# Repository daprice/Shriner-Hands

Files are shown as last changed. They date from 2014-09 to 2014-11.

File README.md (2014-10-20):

#Low Profile Thumb Prosthesis

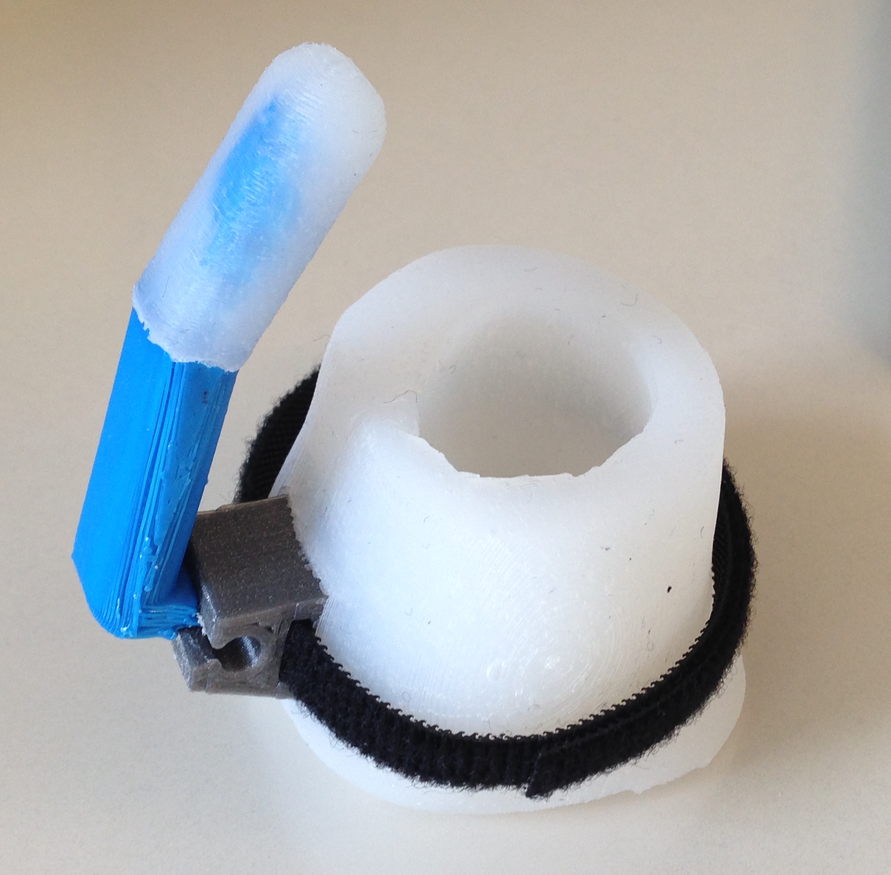
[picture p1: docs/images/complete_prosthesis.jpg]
Photo of assembled prosthesis


This prosthesis is designed to provide a static thumb post for patients who have one or more fingers with a good range of motion, but no thumb to oppose against. The prosthesis consists of a silicone sleeve that goes around the patient's palm, tightened by a velcro strap. A mounting point for a static thumb post (optionally with a grippy silicone cover) is molded into the sleeve.

See the [assembly documentation](http://daprice.github.io/Shriner-Hands/docs/documentation.html) for more information and instructions for configuring and assembling one.

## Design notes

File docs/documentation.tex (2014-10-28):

\documentclass[11pt]{article}
\usepackage[latin2]{inputenc}
\usepackage{a4wide}
\usepackage{graphicx}
\usepackage{hyperref}
\hypersetup{colorlinks=true,linkcolor=blue}
\title{Low Profile Thumb Prosthesis Documentation}
\author{ThingDoc}

\begin{document}

\maketitle
\begin{center}
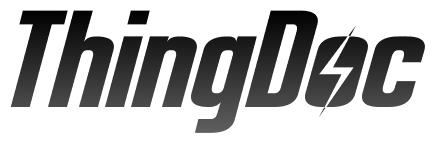
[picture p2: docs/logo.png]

\end{center}
This prosthesis is designed to provide a static thumb post for patients who have one or more fingers with a good range of motion, but no thumb to oppose against. The prosthesis consists of a silicone sleeve that goes around the patient's palm, tightened by a velcro strap. A mounting point for a static thumb post (optionally with a grippy silicone cover) is molded into the sleeve.

\newpage

\tableofcontents

\newpage

\section{Bill of Materials}
List of things you need to build the machine divided by categories.

\subsection{Prerequisites!}
\begin{itemize}
\item 1x \hyperlink{thing_hand\_scan}{3D scan of patient's hand}
\end{itemize}

\subsection{Materials}
\begin{itemize}
\item 100x \hyperlink{thing_g\_dragon\_skin\_30}{grams of Dragon Skin 30 liquid silicone}
\item 10x \hyperlink{thing_g\_dragon\_skin\_10}{grams of Dragon Skin 10 liquid silicone}
\end{itemize}

\subsection{Fasteners}
\begin{itemize}
\item 4x M4 Hex Nut
\item 1x \hyperlink{thing_velcro\_strap}{Velcro Strap}
\item 6x Piece of Tape
\item 4x M4x15 Bolt
\end{itemize}

\subsection{Printed}
\begin{itemize}
\item 2x \hyperlink{thing_rigid\_base}{Rigid base with thumb}
\item 1x \hyperlink{thing_mold\_left\_half}{Mold - left half}
\item 1x \hyperlink{thing_truncated\_hand}{Truncated Print of Patient's Hand}
\item 1x \hyperlink{thing_thumb\_mold}{Thumb Mold}
\item 1x \hyperlink{thing_mold\_right\_half}{Mold - right half}
\end{itemize}

\newpage

\section{Things Overview}
List of things and their descriptions.

\hypertarget{thing_config\_file}{\subsection{Configuration and Rendering of 3D models}}
Configuration settings for the Shriners Hand, required to generate correct STLs of the printed parts. See the Configuration File Assembly instructions to set this up.

\hypertarget{thing_rigid\_base}{\subsection{Rigid base with thumb}}
3D printed rigid base and static thumb post - rendered from src/scad/rigid_base.scad


\hypertarget{thing_silicone\_sleeve}{\subsection{Silicone sleeve}}
Silicone sleeve that goes over the patient's palm

\hypertarget{thing_molded\_thumb}{\subsection{Thumb with Molded Grip}}
Molded silicone thumb pad can improve grip and provide some tactile feedback to the wearer

\hypertarget{thing_truncated\_hand}{\subsection{Truncated Print of Patient's Hand}}
Shortened and resized portion of the patient's palm to be the center of the mold during silicone casting - rendered from src/scad/truncated_hand.scad (example shown)


\hypertarget{thing_thumb\_mold}{\subsection{Thumb Mold}}
Mold for casting the silicone finger tip grip - rendered from src/inventor/thumb_mold.ipt


\hypertarget{thing_g\_dragon\_skin\_10}{\subsection{grams of Dragon Skin 10 liquid silicone}}
Dragon Skin 10 silicone resin kit, available from Smooth-On. Shore A durometer (hardness) 10.
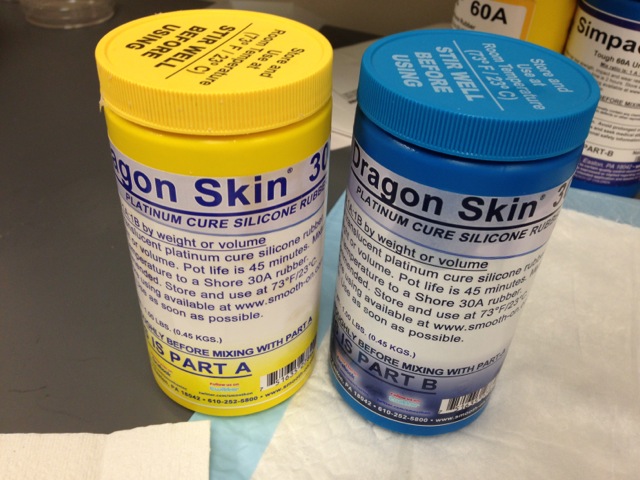
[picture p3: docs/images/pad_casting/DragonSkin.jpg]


\hypertarget{thing_mold\_right\_half}{\subsection{Mold - right half}}
Right half of 3D printed mold for casting the silicone sleeve - rendered from src/scad/mold_right.scad


\hypertarget{thing_mold\_left\_half}{\subsection{Mold - left half}}
Left half of 3D printed mold for casting the silicone sleeve - rendered from src/scad/mold_left_half.scad


\hypertarget{thing_g\_dragon\_skin\_30}{\subsection{grams of Dragon Skin 30 liquid silicone}}
Dragon Skin 30 silicone resin kit, available from Smooth-On. Shore A durometer (hardness) 30.


\hypertarget{thing_velcro\_strap}{\subsection{Velcro Strap}}
9mm wide velcro strap of adequate length to wrap around the patient's palm with at least 30% extra.

\hypertarget{thing_hand\_scan}{\subsection{3D scan of patient's hand}}
3D scan of the patient's hand with wrist and finger(s) held straight. Must be a manifold mesh (STL file); may be simplified for faster processing. Place in userScans directory before configuring and rendering OpenSCAD models.

\hypertarget{thing_mold\_assembly}{\subsection{Palm Sleeve Mold Assembly}}
Assembled mold for casting the silicone sleeve

\newpage

\section{Assembly Instructions}

\subsection{Assemble Configuration and Rendering of 3D models}
Things needed:
\begin{itemize}
\item 1x \hyperlink{thing_hand\_scan}{3D scan of patient's hand}
\end{itemize}
Steps:
\begin{enumerate}
\item Place a manifold, cleaned-up version of the patient's hand scan (if necessary, the model can be repaired using Netfabb) in the userScans folder.
\item Open src/scad/configuration.scad in your favorite text editor.
\item Type the filename of the patient's hand scan in place of "JudahLeftHandShortened.stl" in the configuration file.
\item Open src/scad/alignment.scad using OpenSCAD so you can see the placement of the 3D model while you edit the configuration file. (you may have to manually press the Reload and Preview button every time you make a change to the configuration file)
\item In configuration.scad, change the hand\_d parameter to the diameter of the thickest part of the patient's hand in mm.
\item Adjust the hand\_pos (position of the hand in 3D space) and hand\_rot (rotation of hand around each axis) parameters so that the 3D scan of the hand is aligned with the arrows as described in the following 2 steps.
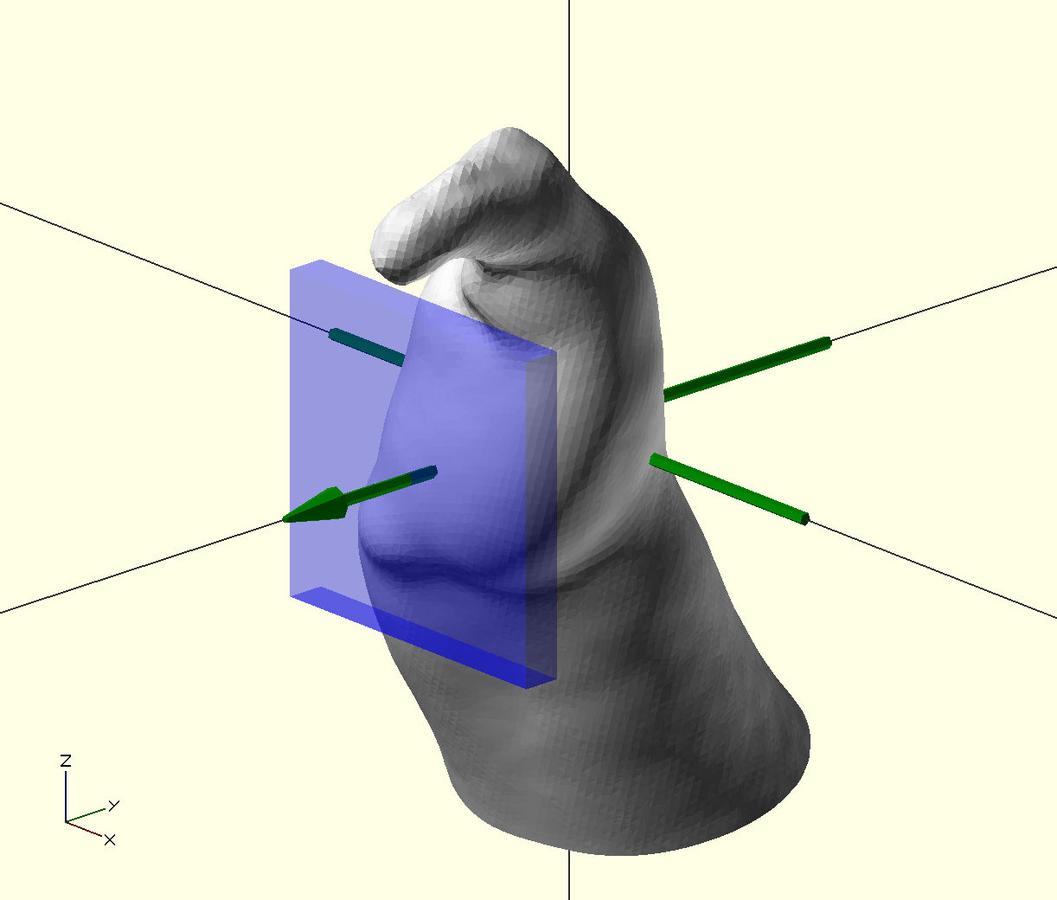
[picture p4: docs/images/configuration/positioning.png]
\item The palm of the hand should be roughly vertical, centered on the green crosshair as much as possible, and the hand should be oriented so that the patient's finger(s) flex toward the green arrow.\\ 
\item The palmar surface should be just within the blue area when viewed from the side.\\ 
\item (Optional) Adjust the other parameters in the configuration file to control the dimensions of various parts of the prosthesis. The default values should work most of the time.
\item After you have aligned the hand, open src/scad/preview.scad in OpenSCAD to ensure that all parts of the prosthesis look correct.\\ 
\item Open each part to be printed (from the src/scad folder) in OpenSCAD, render each one (F6) and export as STL, then print using the STL files. Recommended print settings are 0.2mm or smaller layer height, three perimeters, three top and bottom solid layers, 40\% rectilinear or hexagonal infill, and support material enabled.
\end{enumerate}

\subsection{Assemble Palm Sleeve Mold Assembly}
Things needed:
\begin{itemize}
\item 1x \hyperlink{thing_config\_file}{Configuration and Rendering of 3D models}
\item 4x M4 Hex Nut
\item 1x \hyperlink{thing_mold\_left\_half}{Mold - left half}
\item 1x \hyperlink{thing_rigid\_base}{Rigid base with thumb}
\item 4x Piece of Tape
\item 1x \hyperlink{thing_mold\_right\_half}{Mold - right half}
\item 4x M4x15 Bolt
\end{itemize}
Steps:
\begin{enumerate}
\item Set one half of the mold on a flat surface with the flat side down.
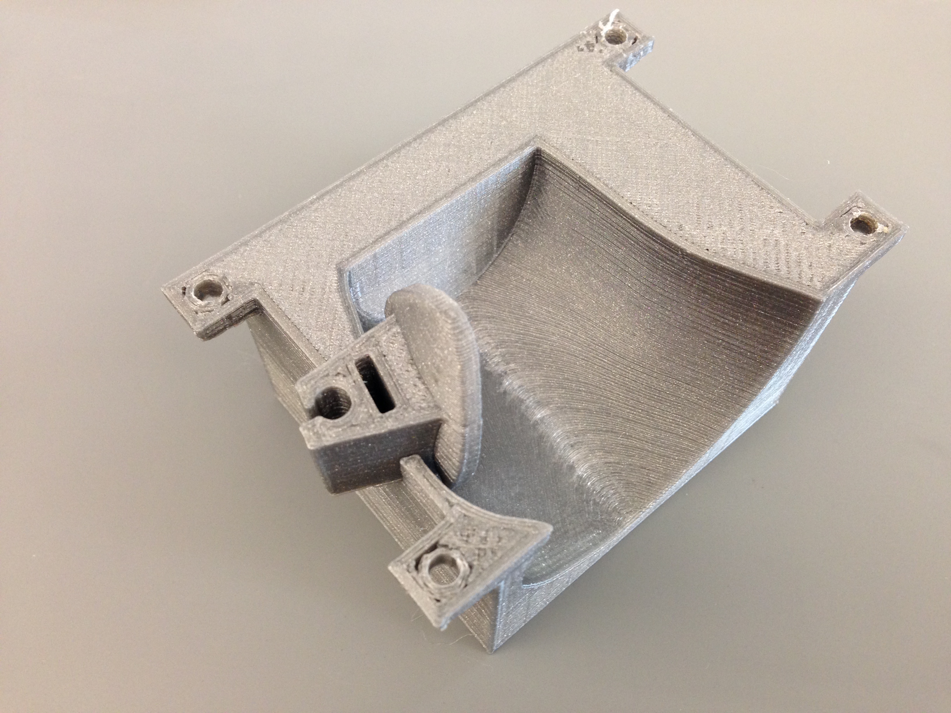
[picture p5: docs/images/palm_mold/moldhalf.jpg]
\item Insert the rigid thumb base into the slot in the side of the mold, with the round part toward the inside and the shorter prong toward the closed end of the mold.\\ 
\item Set the other half of the mold with the flat side up so the two halves align.
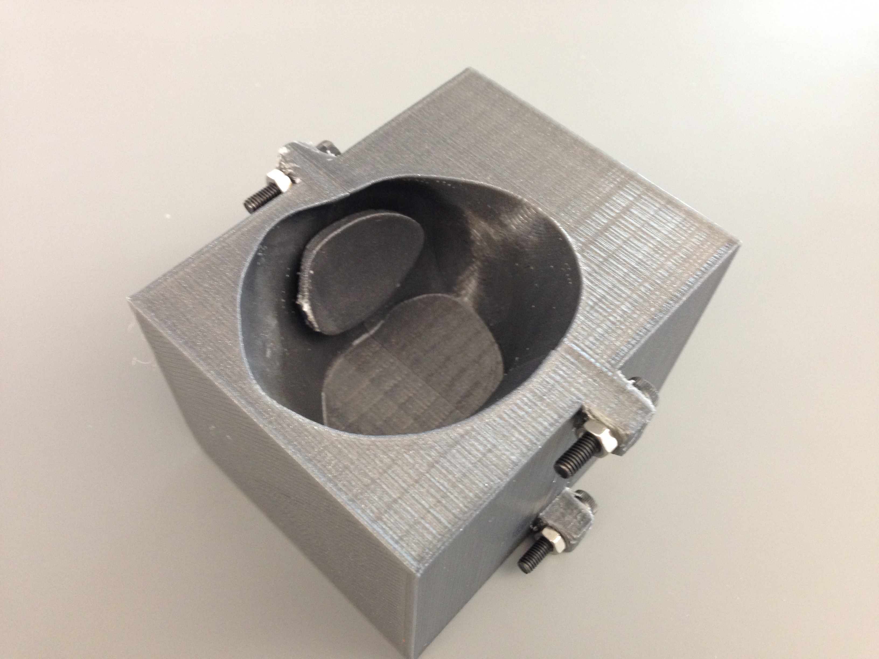
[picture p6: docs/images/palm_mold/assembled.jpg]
\item Fasten the two halves together using the nuts and bolts in the holes at each corner.\\ 
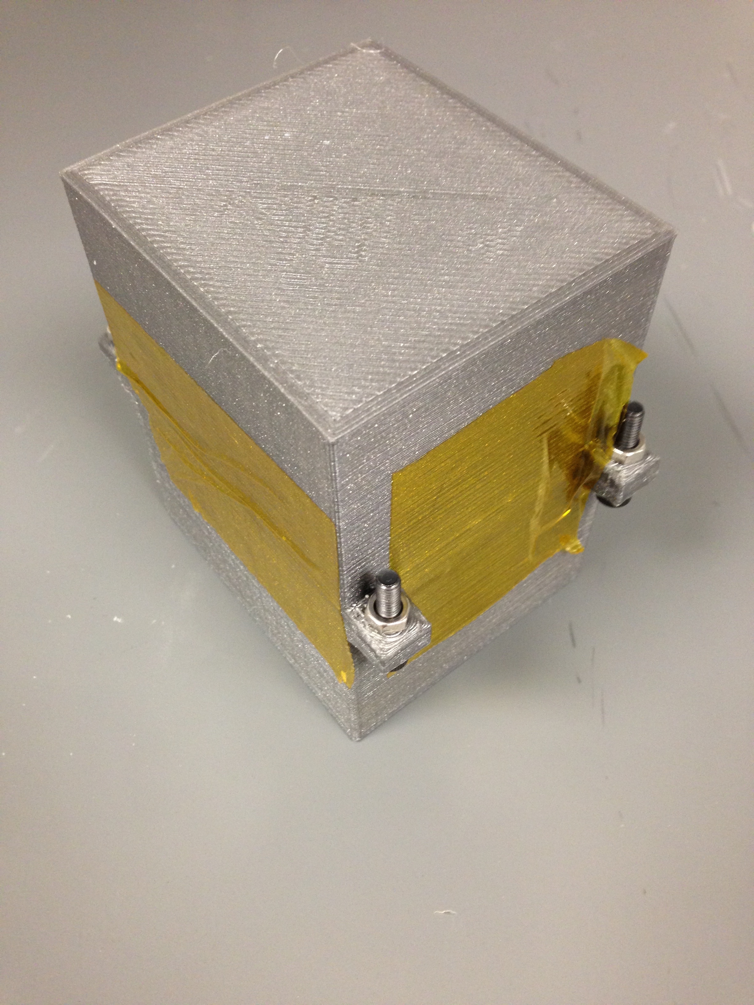
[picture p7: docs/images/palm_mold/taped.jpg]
\item (Optional) use tape to seal the seams on the outside of the mold to prevent leakage.\\ 
\end{enumerate}

\subsection{Assemble Silicone sleeve}
Things needed:
\begin{itemize}
\item 100x \hyperlink{thing_g\_dragon\_skin\_30}{grams of Dragon Skin 30 liquid silicone}
\item 1x \hyperlink{thing_mold\_assembly}{Palm Sleeve Mold Assembly}
\item 1x \hyperlink{thing_truncated\_hand}{Truncated Print of Patient's Hand}
\item 2x Piece of Tape
\end{itemize}
Steps:
\begin{enumerate}
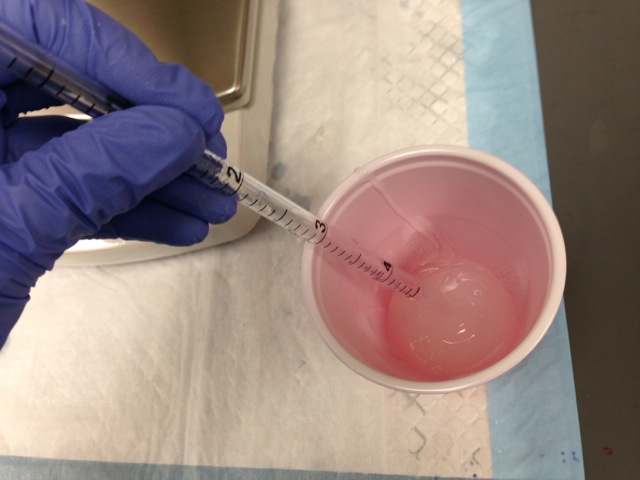
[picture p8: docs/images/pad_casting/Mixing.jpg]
\item Mix silicone according to the instructions from the supplier. Wear gloves and follow the supplier's safety guidelines while working with liquid silicone.\\ 
\item Insert the truncated hand (automatically sized by truncated\_hand.scad) in the opening of the mold, narrow side down, so that it sits in the center of the mold and lines up with the overall shape of the mold. Make sure there is a small gap between the truncated hand and the thumb base piece.\\ 
\item Tape the truncated hand in place to prevent it from moving or floating when the silicone is poured. Leave some space around it open to pour the silicone and for air to escape.\\ 
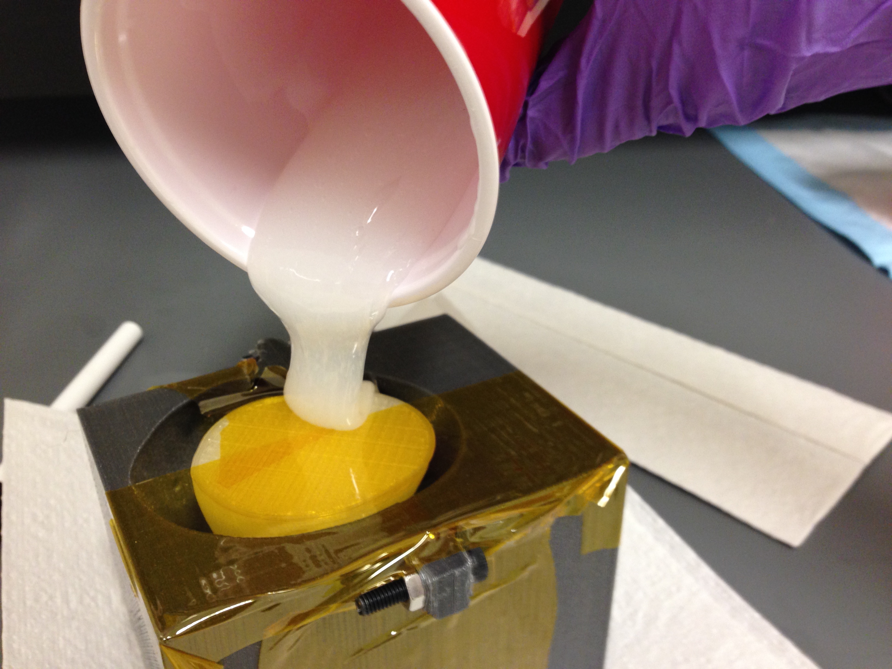
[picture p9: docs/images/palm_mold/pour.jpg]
\item Pour the liquid silicone to fill the mold. Make sure it settles to the bottom and completely surrounds the printed hand.\\ 
\item After the silicone cures (16 hours if using Dragon Skin 30), unscrew and separate the two halves of the mold, and pull out the truncated hand.
\item If necessary, use a knife to cut off any excess silicone and/or cut the sleeve to better fit the patient's hand.
\end{enumerate}

\subsection{Assemble Thumb with Molded Grip}
Things needed:
\begin{itemize}
\item 1x \hyperlink{thing_rigid\_base}{Rigid base with thumb}
\item 10x \hyperlink{thing_g\_dragon\_skin\_10}{grams of Dragon Skin 10 liquid silicone}
\item 1x \hyperlink{thing_thumb\_mold}{Thumb Mold}
\end{itemize}
Steps:
\begin{enumerate}
\item Print the skeletal thumb and mold.
\item Mix silicone according to the instructions from the supplier. Wear gloves and follow the supplier's safety guidelines while working with liquid silicone.\\ 
\item Pour the liquid silicone to mostly fill the thumb mold.
\item Insert the printed skeletal thumb into the filled mold as far as it will go.
\item Remove most of the excess silicone. Small amounts of excess can be removed afer molding.
\item After the silicone has cured (up to 7 hours if using Dragon Skin 10 Slow), carefully pull the thumb to remove it from the mold.
\item If necessary, use a knife to trim off excess silicone so that the edges of the silicone part are flush with those of the hard printed part.
\end{enumerate}

\subsection{Assemble Low Profile Thumb Prosthesis}
Things needed:
\begin{itemize}
\item 1x \hyperlink{thing_silicone\_sleeve}{Silicone sleeve}
\item 1x \hyperlink{thing_molded\_thumb}{Thumb with Molded Grip}
\item 1x \hyperlink{thing_velcro\_strap}{Velcro Strap}
\end{itemize}
Steps:
\begin{enumerate}
\item Insert the thumb into the slot on the base.
\item Insert the velcro strap through the slot on the base.
\item (Optional) If the velcro strap does not fit well around the silicone sleeve, use a knife to cut slits into the sides of the sleeve, then route the velcro sleeve through the slits.
\item Insert patient's hand into the sleeve.
\item Fasten the velcro strap and tighten as needed to hold the prosthesis in place during use.
\end{enumerate}

\newpage

\end{document}

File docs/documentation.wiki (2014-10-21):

== Bill of Materials ==

=== Prerequisites! ===
{| class="wikitable sortable" border="1"
|-
! scope="col" | Quantity
! scope="col" | Description
! scope="col" | Type
! scope="col" class="unsortable" | Comments
! scope="col" class="unsortable" | Diagram
|-
| 1 || 3D scan of patient's hand ||  ||  ||
|}

=== Materials ===
{| class="wikitable sortable" border="1"
|-
! scope="col" | Quantity
! scope="col" | Description
! scope="col" | Type
! scope="col" class="unsortable" | Comments
! scope="col" class="unsortable" | Diagram
|-
| 100 || grams of Dragon Skin 30 liquid silicone ||  ||  || 50px
|-
| 10 || grams of Dragon Skin 10 liquid silicone ||  ||  || 50px
|}

=== Fasteners ===
{| class="wikitable sortable" border="1"
|-
! scope="col" | Quantity
! scope="col" | Description
! scope="col" | Type
! scope="col" class="unsortable" | Comments
! scope="col" class="unsortable" | Diagram
|-
| 4 || M4 Hex Nut ||  ||  ||
|-
| 1 || Velcro Strap ||  ||  ||
|-
| 6 || Piece of Tape ||  ||  ||
|-
| 4 || M4x15 Bolt ||  ||  ||
|}

=== Printed ===
{| class="wikitable sortable" border="1"
|-
! scope="col" | Quantity
! scope="col" | Description
! scope="col" | Type
! scope="col" class="unsortable" | Comments
! scope="col" class="unsortable" | Diagram
|-
| 2 || Rigid base with thumb ||  ||  || 50px
|-
| 1 || Mold - left half ||  ||  || 50px
|-
| 1 || Truncated Print of Patient's Hand ||  ||  || 50px
|-
| 1 || Thumb Mold ||  ||  || 50px
|-
| 1 || Mold - right half ||  ||  || 50px
|}

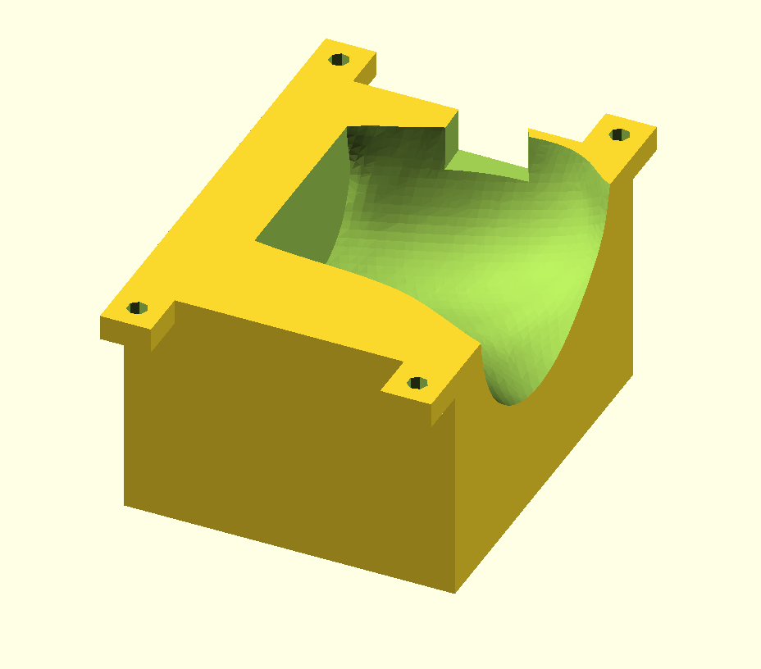
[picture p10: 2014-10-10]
docs/images/mold_right_half.png

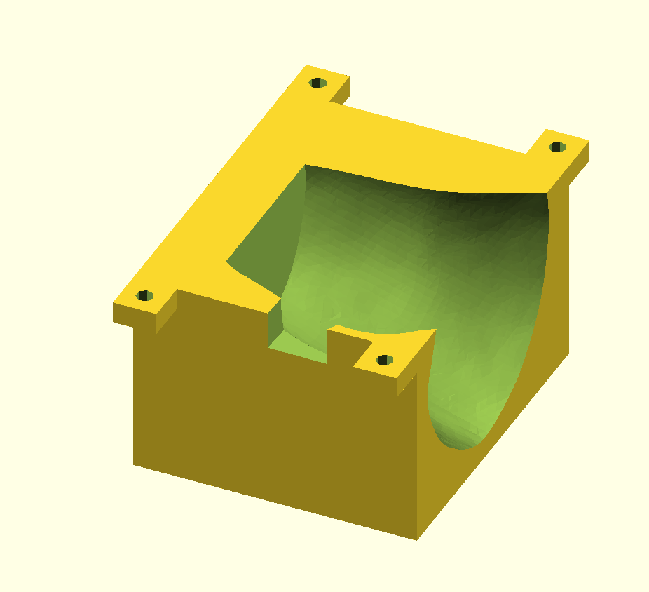
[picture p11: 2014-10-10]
docs/images/mold_left_half.png

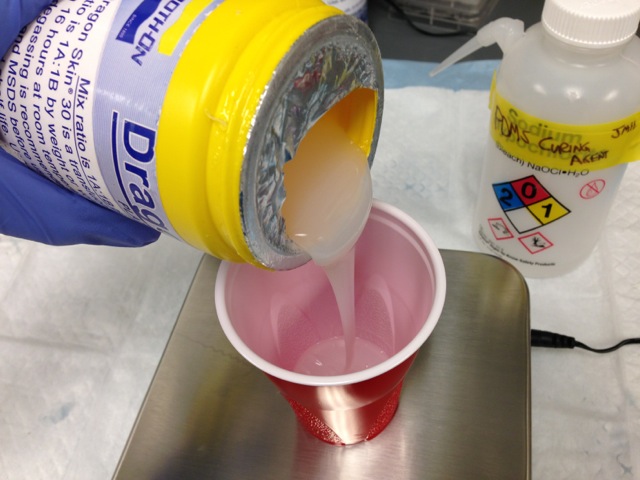
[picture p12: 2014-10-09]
docs/images/pad_casting/Pouring part A.jpg

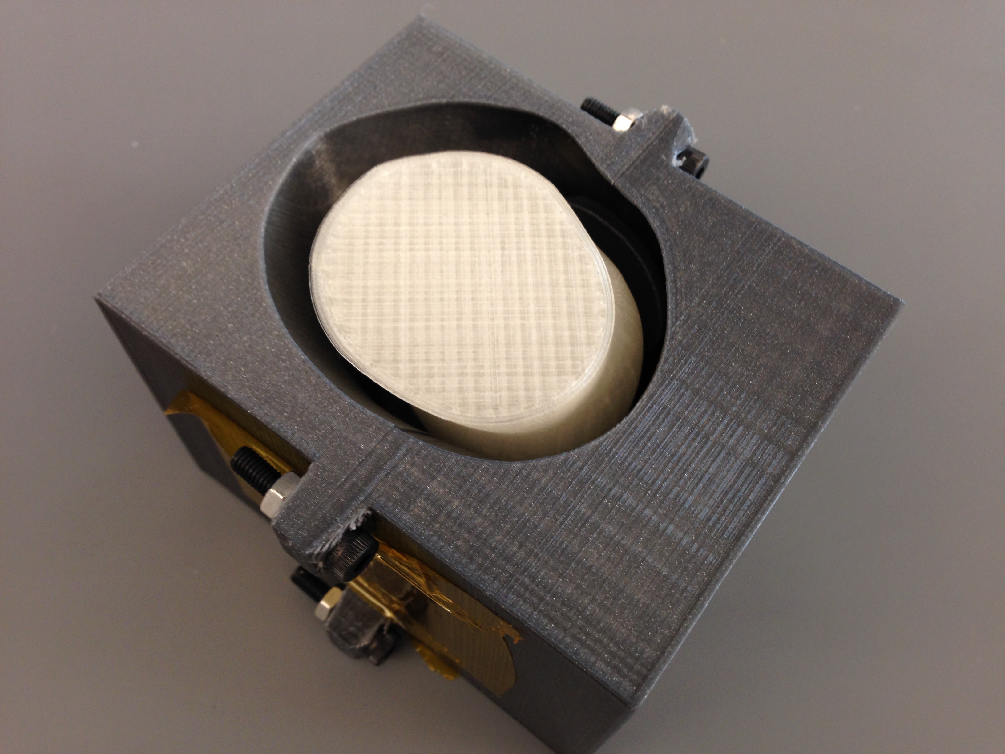
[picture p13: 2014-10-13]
docs/images/palm_mold/hand_in_mold.jpg

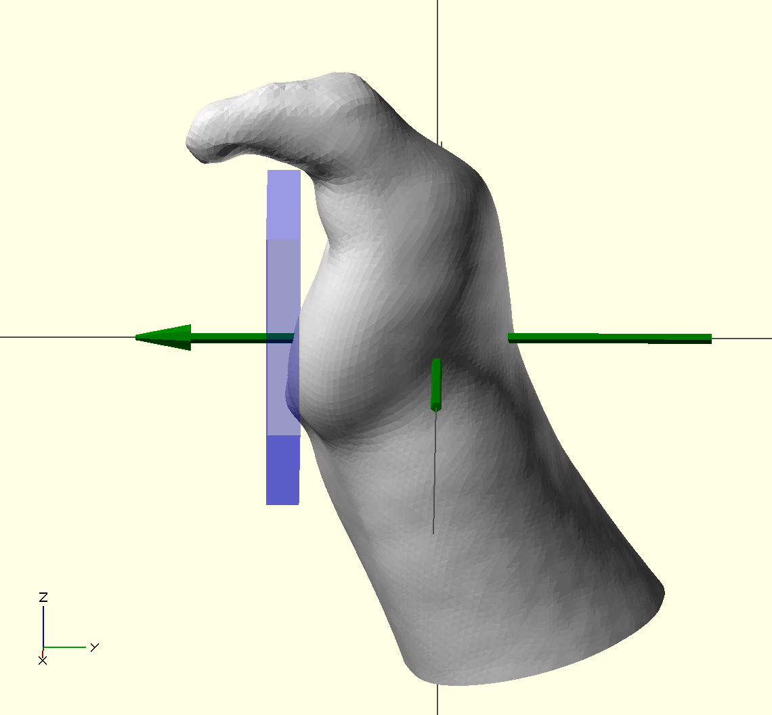
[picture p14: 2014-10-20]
docs/images/configuration/forward_alignment.png

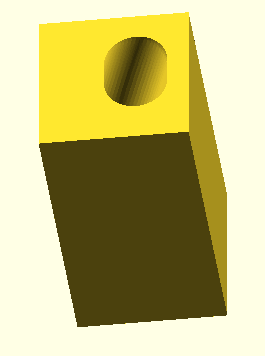
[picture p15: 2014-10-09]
docs/images/thumb_mold.png

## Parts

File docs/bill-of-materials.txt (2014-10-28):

Bill of Materials: Low Profile Thumb Prosthesis
+++++++++++++++++++++++++++++++++++++++++++++++

Prerequisites!
==============
- 1x 3D scan of patient's hand

Materials
=========
- 100x grams of Dragon Skin 30 liquid silicone
- 10x grams of Dragon Skin 10 liquid silicone

Fasteners
=========
- 4x M4 Hex Nut
- 1x Velcro Strap
- 6x Piece of Tape
- 4x M4x15 Bolt

Printed
=======
- 2x Rigid base with thumb
- 1x Mold - left half
- 1x Truncated Print of Patient's Hand
- 1x Thumb Mold
- 1x Mold - right half

----
Generated on 2014/10/28 17:28:17 by ThingDoc - http://thingdoc.org/

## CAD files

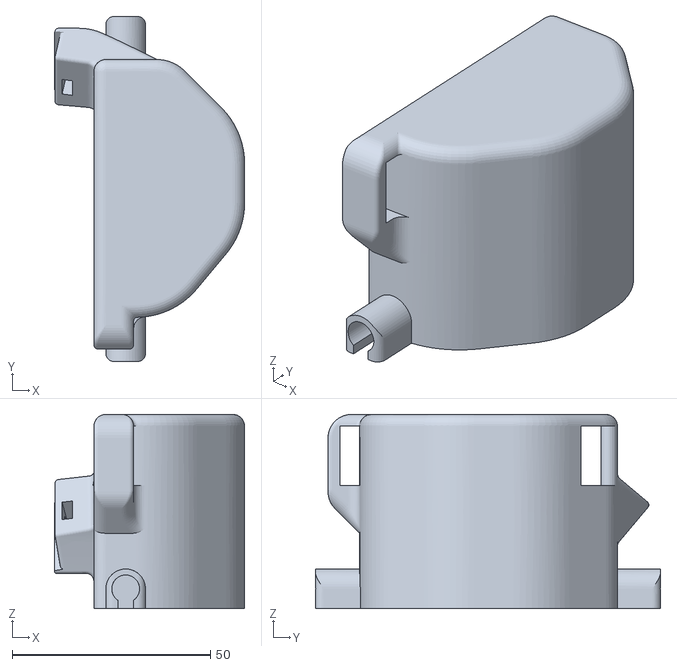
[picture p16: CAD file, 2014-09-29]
palm_blank.stl
48.0 x 87.0 x 49.0

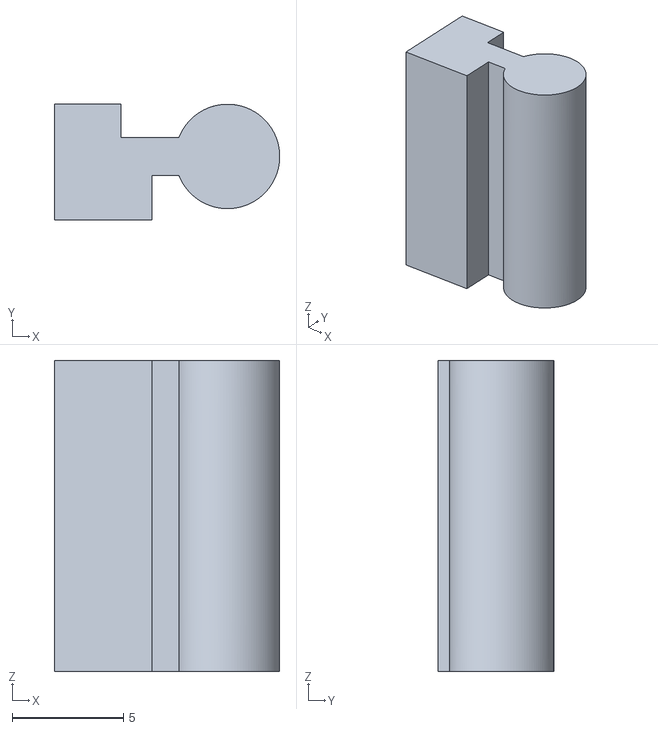
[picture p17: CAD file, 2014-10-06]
src/inventor/rigid connector.stl
10.2 x 5.20 x 14.0

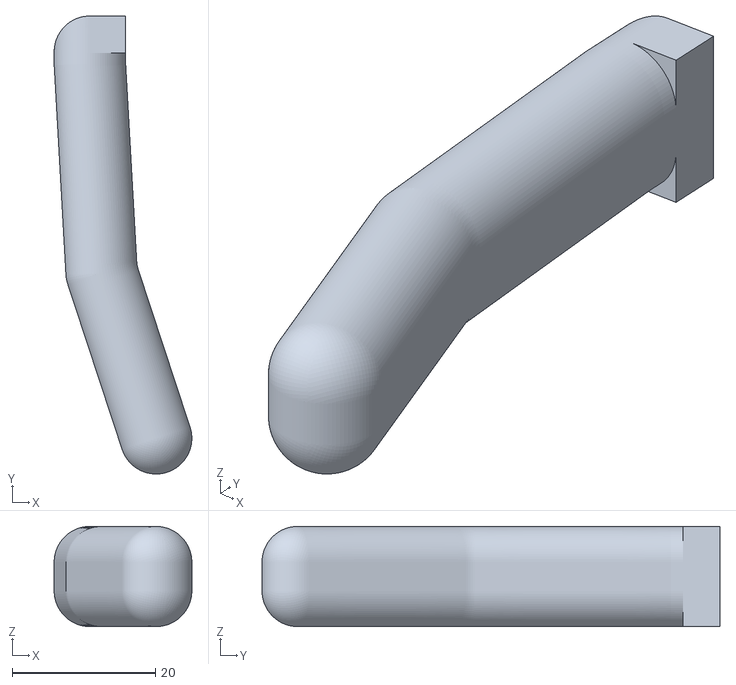
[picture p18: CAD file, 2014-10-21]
src/inventor/thumb without grip/60mm.stl
19.2 x 64.0 x 14.0

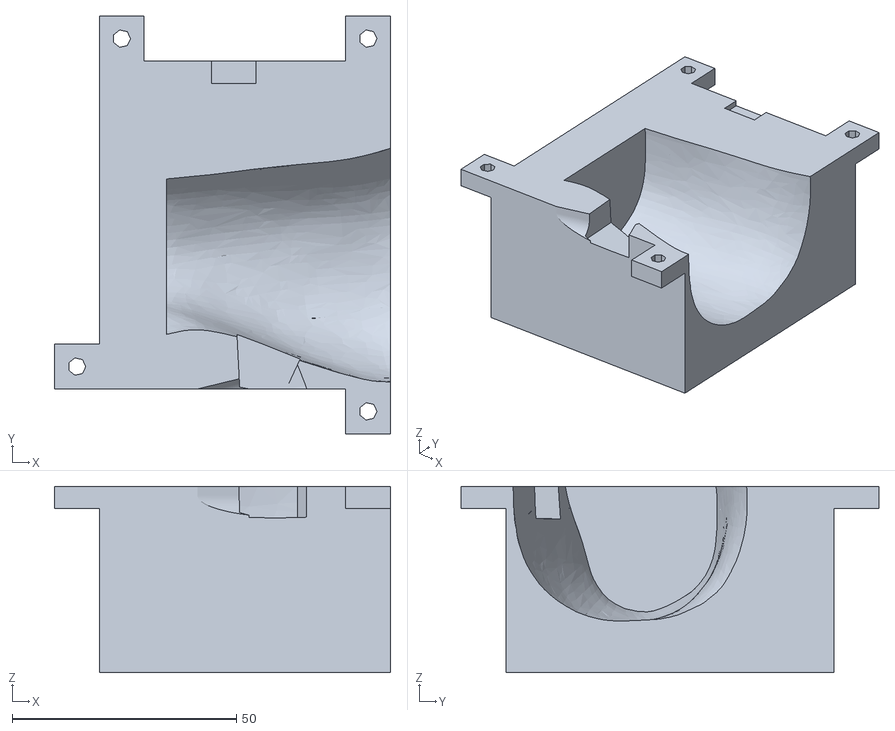
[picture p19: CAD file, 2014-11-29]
stl/mold_left_half.stl
75.0 x 93.2 x 41.6

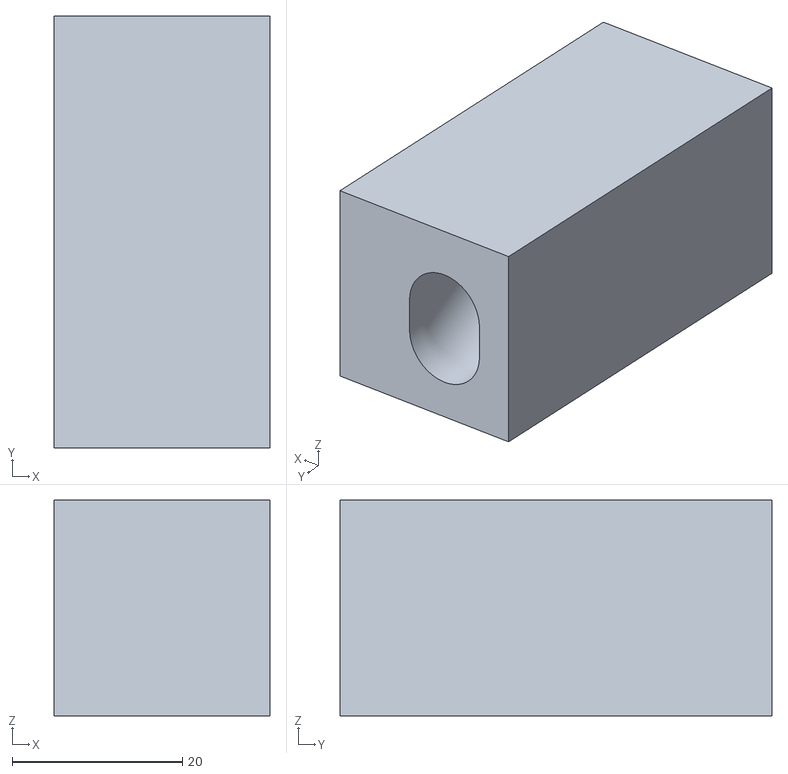
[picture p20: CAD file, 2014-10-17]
stl/thumb with grip/40mm_mold.stl
25.4 x 50.8 x 25.4

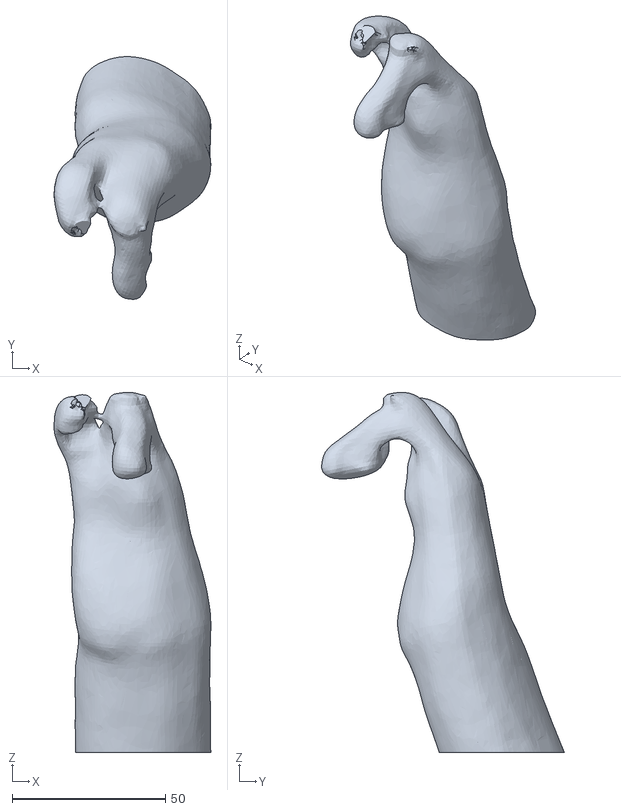
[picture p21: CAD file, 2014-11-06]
userScans/mercy_right_hand.stl
51.3 x 79.3 x 117.6

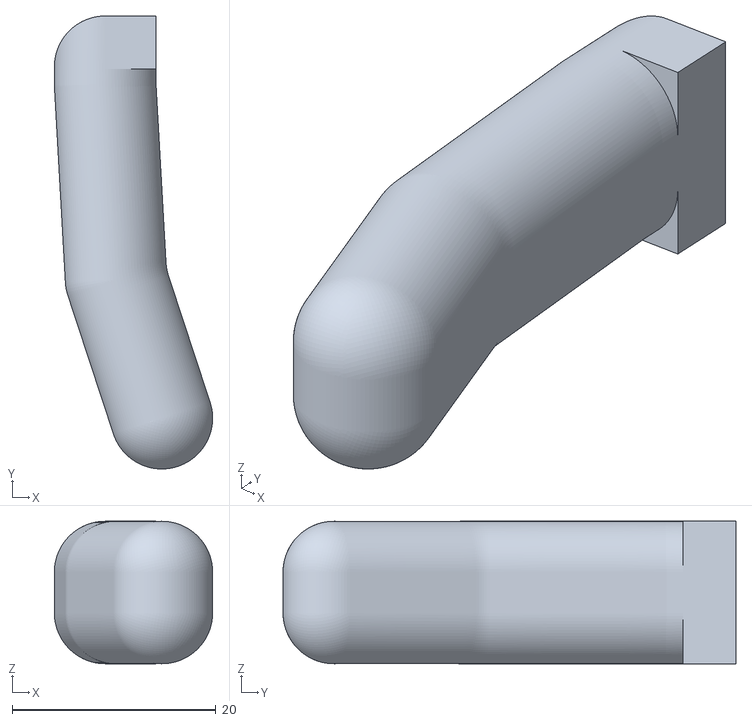
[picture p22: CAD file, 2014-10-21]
src/inventor/thumb without grip/40mm.stl
15.6 x 44.5 x 14.0

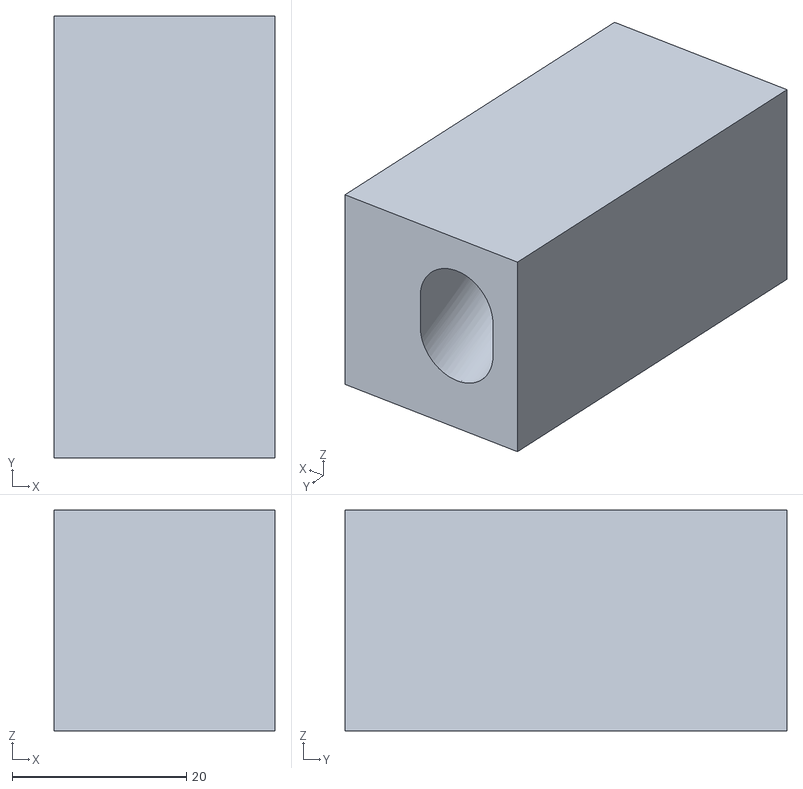
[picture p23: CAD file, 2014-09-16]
stl/thumb with grip/60mm_mold.stl
25.4 x 50.8 x 25.4

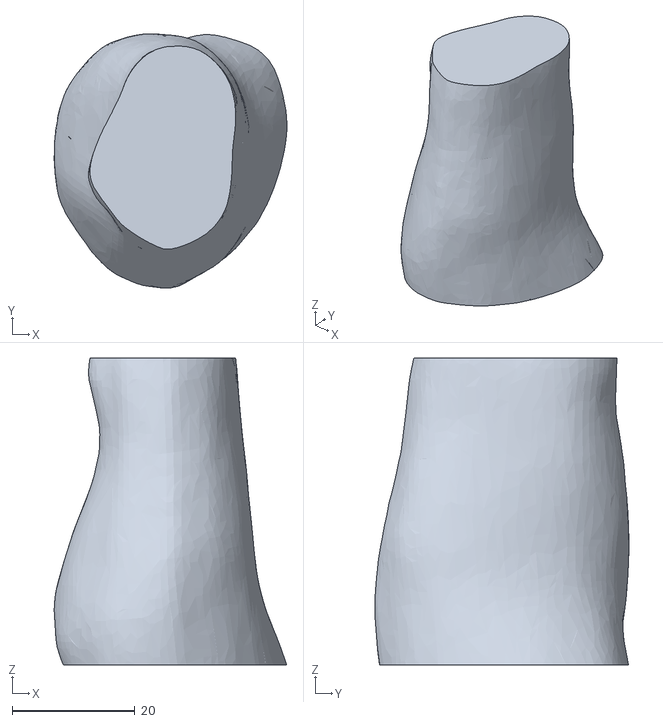
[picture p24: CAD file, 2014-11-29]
stl/truncated_hand.stl
37.9 x 41.4 x 50.0

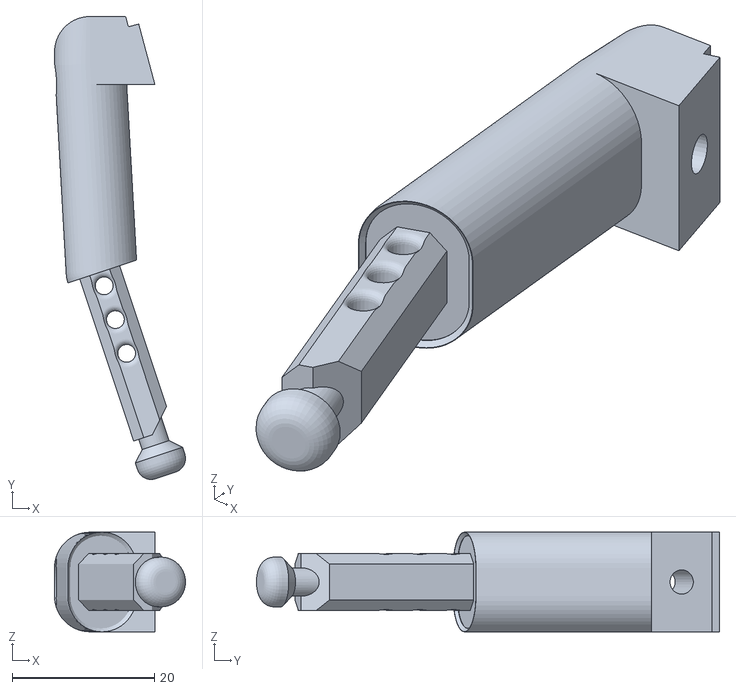
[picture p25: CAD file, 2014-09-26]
thumb_with_grip_cutout.stl
18.4 x 65.0 x 14.0

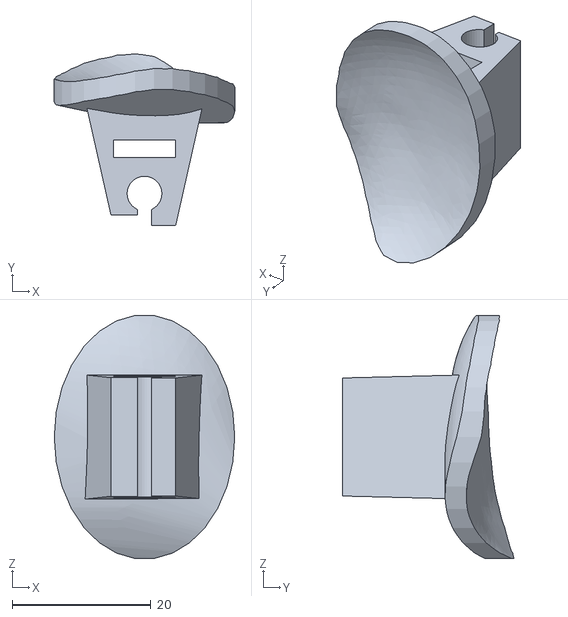
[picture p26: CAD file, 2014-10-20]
stl/rigid_base.stl
26.0 x 24.7 x 35.0

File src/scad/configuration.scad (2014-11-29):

// Hand alignment parameters:

hand_scan = "../../userScans/mercy_right_hand.stl"; //location of STL of patient's hand scan

hand_d = 38; //diameter of the thickest part of the patient's hand in mm
hand_pos = [17,5,-220]; //position of the hand in X,Y,Z axis so that the palm is centered on the Z axis and aligned with the thumb piece in preview.scad
hand_rot = [-5,4,-90]; //rotation of hand scan about each axis so that the patient's finger(s) oppose the thumb post in preview.scad

palm_h = 50; //height of the area of the palm to be covered by the silicone

//=============================

// Design parameters:

base_thickness = 3; //thickness of the rigid base oval
base_h = 26; //height of the rigid base oval
base_w = 35; //width of the rigid base oval

thumb_depth = 17; //amount the thumb mount sticks out from the palm
thumb_angle = 11; //angle of the complete thumb and base from vertical towards the patient's palm/finger(s)
thumb_outward_angle = 30; //angle of the thumb post away from the hand
thumb_length = "short"; //"long" (60mm) or "short" (40mm)
thumb_grip = true; //whether the thumb should allow for casting a grippy pad or not

outer_scale = 1.4; //scale of outside surface of prosthesis relative to the patient's hand
inner_scale = 0.93; //scale of inside surface of prosthesis relative to the patient's hand (<1 results in a tighter fit by compensating for the stretchiness of the silicone)

wearing = true; //whether or not to show the prosthesis being worn by the patient in the preview. Does not affect final renders of parts.


/**
 * Configuration settings for the Shriners Hand, required to generate correct STLs of the printed parts. See the Configuration File Assembly instructions to set this up.
 * @id config_file
 * @name Configuration and Rendering of 3D models
 * @using 1 hand_scan
 * @step Place a manifold, cleaned-up version of the patient's hand scan (if necessary, the model can be repaired using Netfabb) in the userScans folder.
 * @step Open src/scad/configuration.scad in your favorite text editor.
 * @step Type the filename of the patient's hand scan in place of "JudahLeftHandShortened.stl" in the configuration file.
 * @step Open src/scad/alignment.scad using OpenSCAD so you can see the placement of the 3D model while you edit the configuration file. (you may have to manually press the Reload and Preview button every time you make a change to the configuration file)
 * @step In configuration.scad, change the hand_d parameter to the diameter of the thickest part of the patient's hand in mm.
 * @step Adjust the hand_pos (position of the hand in 3D space) and hand_rot (rotation of hand around each axis) parameters so that the 3D scan of the hand is aligned with the arrows as described in the following 2 steps.
 * @step The palm of the hand should be roughly vertical, centered on the green crosshair as much as possible, and the hand should be oriented so that the patient's finger(s) flex toward the green arrow. [[configuration/positioning.png]]
 * @step The palmar surface should be just within the blue area when viewed from the side. [[configuration/forward_alignment.png]]
 * @step (Optional) Adjust the other parameters in the configuration file to control the dimensions of various parts of the prosthesis. The default values should work most of the time.
 * @step After you have aligned the hand, open src/scad/preview.scad in OpenSCAD to ensure that all parts of the prosthesis look correct. [[configuration/assembly_preview.png]]
 * @step Open each part to be printed (from the src/scad folder) in OpenSCAD, render each one (F6) and export as STL, then print using the STL files. Recommended print settings are 0.2mm or smaller layer height, three perimeters, three top and bottom solid layers, 40% rectilinear or hexagonal infill, and support material enabled.
 */

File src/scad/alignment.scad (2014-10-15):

//Assists in positioning the hand scan to align the prosthesis with the patient's hand.
// by Dale Price

include <configuration.scad>;
use <misc.scad>;

color("lightgray") translate([0, -hand_d/2, 0]) rotate([0,0,90]) hand_scan();

//visual aids for alignment
color("green") rotate([0,90,0]) cylinder(h=hand_d*2, d=2, center=true);
color("green") rotate([90,0,0]) cylinder(h=hand_d*2, d=2, center=true);
color("green") translate([0,-hand_d,0]) rotate([90,0,0]) cylinder(d1=5,d2=1,h=10,center=true);
color([0,0,1,0.4]) translate([0,(-hand_d*inner_scale - hand_d*outer_scale)/4, 0]) cube([palm_h,6,palm_h], center=true);

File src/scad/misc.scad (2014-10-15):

//miscellaneous functions to help with generating prostheses
// by Dale Price

include <configuration.scad>;

module hand_scan(scale=1) //places the wearer's hand scan with selected position from configuration.scad
{
	scale(scale) translate(hand_pos) rotate(hand_rot) import(hand_scan, convexity=10);
}

module truncated_scan(scale=1) //places the relevant section of the wearer's hand
{
	intersection() {
		cube([500,500,palm_h], center=true);
		hand_scan(scale=scale);
	}
}


module smooth_scan(scale=1) //places a smoothed out version of the wearer's palm using hull()
{
	hull() {
		truncated_scan(scale=scale);	
	}
}

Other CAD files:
stl/mold_right_half.stl
src/scad/mold_left_half.scad
src/inventor/rigid connector.ipt
src/inventor/thumb2.ipt
src/inventor/thumb_mold.ipt
src/inventor/thumb_with_grip_cutout.ipt
src/scad/mold_right_half.scad
src/scad/preview.scad
src/scad/rigid_base.scad
src/scad/truncated_hand.scad

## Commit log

2014-09-16 Design printable attachment for filaflex joint that can be glued onto thermoplastic gauntlet
    [filaflex_wrist_joint.stl, gauntlet_attachment.stl, new_palm.ipt]
2014-09-19 Update finger attachment to use M3 socket head cap screw
    [hand_assembly.iam, new_palm.ipt, rigid connector.ipt, thumb2.ipt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]
2014-09-22 Adjust angle of thumb
    [hand_assembly.iam, new_palm.ipt, rigid connector.ipt, thumb2.ipt]
2014-09-23 Misc updates
    [hand_assembly.iam, new_palm.ipt]
2014-09-23 add palm piece without cutout so the wearer's palm can be subtracted by other means
    [palm_blank.ipt, palm_blank.stl]
2014-09-24 test openscad script to cut the shape of the palm piece from a 3D scan
    [JudahRightHand.stl, Left.scad, cut_palm.scad]
2014-09-24 refactor openscad
    [Left.scad, cut_palm.scad]
2014-09-26 Add initial prototype hand for Mercy
    [MercyRightHand.stl, mercy_left_hand.stl, mercy_left_hand_repaired.stl]
2014-09-26 Add STLs of molding equipment for making the silicone liner for Mercy's prosthesis
    [mercy_hand_sleeve_molding_helper.stl, mercy_left_hand_for_casting.stl]
2014-09-26 Lengthen skeletal thumb to reduce bending of the silicone at the tip
    [thumb_with_grip_cutout.ipt, thumb_with_grip_cutout.stl]
2014-09-29 further attempt to repair the bad STL generated by Inventor; add thumb STL without grip cutout
    [cut_palm.scad, mercy_left_hand_repaired.stl, palm_blank.stl, palm_blank_repaired.stl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]
2014-10-01 Fix palm blank to be manifold
    [Left.scad, palm_blank.ipt, palm_blank_repaired.stl]
2014-10-01 Add posts to gauntlet attachment piece for secure attachment to a thermoplastic gauntlet
    [gauntlet_attachment.stl]
2014-10-03 Slightly shorten skeletal thumb to thicken the silicone over the tip
    [Left.scad, thumb_with_grip_cutout.ipt]
2014-10-06 Revert to friction fit dogbone shape for thumb post attachment
    [rigid connector (for screw).ipt, rigid connector.ipt, thumb2.ipt, thumb2.stl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]
2014-10-06 Add STL of rigid dogbone connector for use in other modeling tools such as OpenSCAD
    [rigid connector.stl]
2014-10-08 Organize files for low profile thumb prosthesis
    [JudahRightHand.stl, Left.scad, MercyRightHand.stl, configuration.scad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]
2014-10-08 Generate mounting disc for low profile thumb prosthesis
    [configuration.scad, misc.scad, rigid_base.scad]
2014-10-09 Add thumb mounting slot to rigid thumb base
    [configuration.scad, rigid_base.scad]
2014-10-09 Add ThingDoc documentation for parts so far
    [rigid_base.scad]
2014-10-09 Add 3D scan as prerequisite in documentation
    [configuration.scad]
2014-10-09 Add velcro slot to rigid thumb mount
    [configuration.scad, rigid_base.scad]
2014-10-10 Add molding parts and documentation
    [configuration.scad, misc.scad, mold_left_half.scad, mold_right_half.scad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]
2014-10-10 Generate STLs of scad models
    [mold_left_half.stl, mold_right_half.stl, rigid_base.scad, rigid_base.stl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]
2014-10-13 Add photos and improve documentation of palm sleeve molding process – fixes #3
    [mold_left_half.scad]
2014-10-13 Add slot to pry mold open - fixes #1
    [mold_left_half.scad, mold_left_half.stl, mold_right_half.stl]
2014-10-15 Add preview.scad which shows a rendering of the complete prosthesis on the patient's hand
    [configuration.scad, mold_left_half.scad, preview.scad]
2014-10-15 Fix missing coordinate in hand positioning
    [preview.scad]
2014-10-15 Add alignment.scad which aids in the positioning of the hand scan
    [alignment.scad]
2014-10-15 Apply hand rotation before translation to make the position adjustment clearer
    [misc.scad]
2014-10-15 Adjust positioning of hand to compensate for changes made in 7b30a5
    [configuration.scad]
2014-10-17 Redesign thumb slot in openscad instead of using the one from inventor in order to leave space for the printed inventor finger to fit; fixes #5
    [rigid_base.scad, rigid_base.stl]
2014-10-17 fix rotation for printing
    [rigid_base.scad]
2014-10-17 Add multiple versions of the thumb with different lengths
    [40mm.stl, 40mm_mold.stl, 60mm.stl, 60mm_mold.stl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]
2014-10-19 Fix thumb to be in one piece
    [thumb2.ipt, thumb_with_grip_cutout.ipt]
2014-10-20 Fix thumb base rotation for printing
    [rigid_base.stl]
2014-10-20 Document the process of configuring the OpenSCAD models of the prosthesis (fixes #4); add readme with link to documentation
    [configuration.scad, mold_left_half.scad, mold_right_half.scad, rigid_base.scad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]
2014-10-21 Incorporate thumb post into rigid base to print as one piece
    [40mm.stl, 60mm.stl, configuration.scad, mold_left_half.scad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]
2014-10-21 Add ability to angle just the thumb away from the hand (equivalent of thumb flexion/extension)
    [configuration.scad, rigid_base.scad]
2014-10-28 Improve documentation: include STL repair and print setting notes; improve instructions for casting and finishing silicone sleeve
    [configuration.scad, mold_left_half.scad]
2014-11-06 Configure and render hand parts for patient
    [JudahRightHand.stl, configuration.scad, mercy_right_hand.stl, mold_left_half.scad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]
2014-11-28 Adjust thumb positioning/spacing
    [configuration.scad, mold_left_half.scad, mold_left_half.stl, mold_right_half.stl]
2014-11-29 Thicken sleeve; use non-hulled hand scan for generation of thumb base
    [configuration.scad, mold_left_half.stl, mold_right_half.stl, rigid_base.scad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]
